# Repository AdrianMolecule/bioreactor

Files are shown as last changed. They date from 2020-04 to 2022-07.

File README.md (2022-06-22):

# bioreactor
Hi there! Welcome to the Bioreactor repository. While a lot of information is still stored in other repositories like Slack, Google Docs and different clouds this is pretty comprehensive and usable.

Please be aware this is work in progress and sometimes the most recent version is under the cloud storage for the specific application.

For software please look under src firmware for most of the code. You will need to use Eclipse and we have a config guide under docs.
The Blocky interpreter will be added soon and initially will be using Visual Studio but that might change.

For electronics you can find descriptive pdf files for all the boards and the corresponding schematics and PCB layouts under electronics. They don't change a lot, so most likely what you see in here is the latest stable board.

For mechanics you can find the Fusion 360 files for the main body under mechanics. Some of the smaller parts that are 3d printed are designed using Tinkercad. Newer ones are done in Fusion 360 or OpenCad as we move away from Tinkercad.

Most of the images and some videos are under docs images. Sometimes an image is worth 1000 words.

There is a boilerplate paper which highlights the generic editing yet it is is just a place to gather paper materials.

We also have a spreadsheet with the parts yet that is a little bit of a moving target as we enhance the design and experiment with newer parts.

Several folders like management-interface, server and controller contain experimental material

Below you can find a brief info about setting up the device, for other questions feel to shoot [us](https://github.com/liquidatom) a message.

## Quick Start

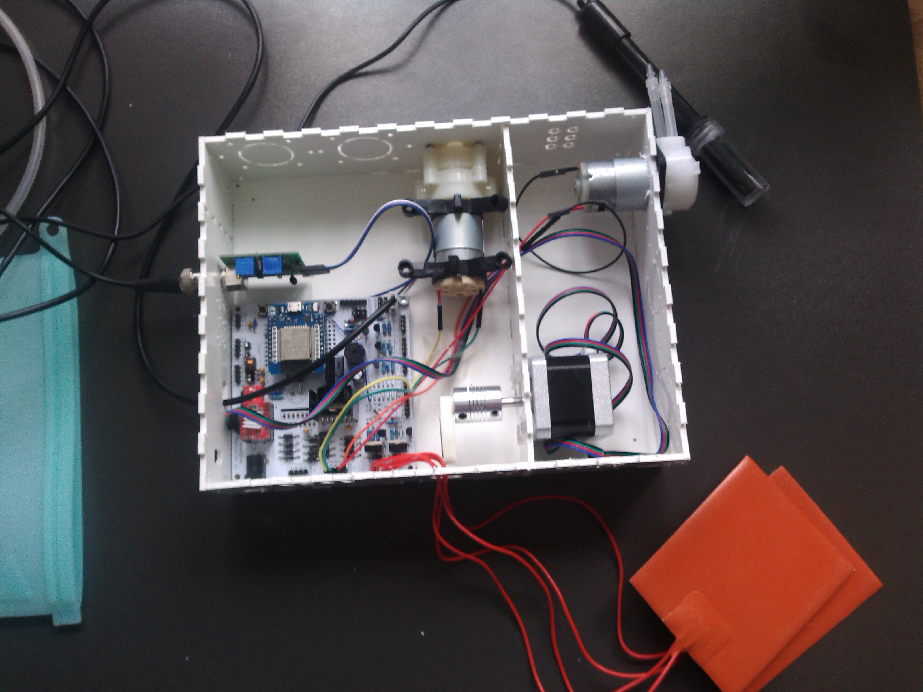
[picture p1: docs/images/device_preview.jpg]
device preview
1. Assemble the device 
2. [Configure eclipse](https://github.com/AdrianMolecule/bioreactor/blob/master/docs/Configuring%20Eclipse%20to%20run%20ESP32.md)  
3. Build and upload firmware
4. Configure bioreactor using [this](https://github.com/AdrianMolecule/bioreactor/tree/master/docs/manual%20bioreactor%20v1.pdf) manual
5. use the ODmeter readme to install the ODMeter

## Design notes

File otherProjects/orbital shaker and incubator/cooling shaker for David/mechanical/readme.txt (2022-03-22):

The f3d files are Fusion360 files for both the CNC machine and 3dPrintig. On request, I can generate stl files for 3d printing and raw files for the specific CNC you have.

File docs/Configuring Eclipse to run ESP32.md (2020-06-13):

This document is about configuring Eclipse to build and run ESP32 firmware. Can be used to configure almost any arduino-like hardware, same way as you can do it in Arduino IDE.

### Prerequirements
I'm using Eclipse 4.15.0, but any with 'Eclipse Marketplace' should work.  
Also i assume your IDE already has C/C++ support, if not, you can easily upgrade it by installing **'Eclipse C/C++ IDE CDT'** plugin from market place

### Steps to run ESP application
1. Open marketplace by clicking Help->Eclipse Marketplace

2. Find and install plugin 'The Arduino Eclipse plugin named Sloeber V4'.  
arduino plugin

3. After installation new menu option 'Arduino' will be added on the top pane. To work with ESP32 you need to open 'Arduino->Preferences->Arduino->Third party index url' and add external url  
<https://adafruit.github.io/arduino-board-index/package_adafruit_index.json>  
<https://raw.githubusercontent.com/espressif/arduino-esp32/gh-pages/package_esp32_index.json>  

4. Then you can enable platform under 'Arduino->Preferences->Arduino->Platforms and Boards' and libraries 'Arduino->Preferences->Arduino->Library Manager'.  
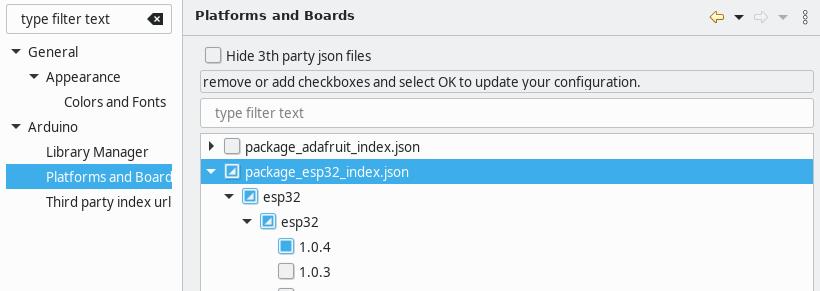
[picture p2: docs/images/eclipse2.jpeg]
sdk lsit
  
There is a useful option 'Arduino->Reattach libraries' which should search through the source code and enable all libraries in Library Manager, though sometimes it misses few of them.

5. After that you just need to import existing project from src/firmware  
If you create a project from scratch, choose File->New->Arduino sketch. In project`s Preferences you want set ESP settings as  depicted below  
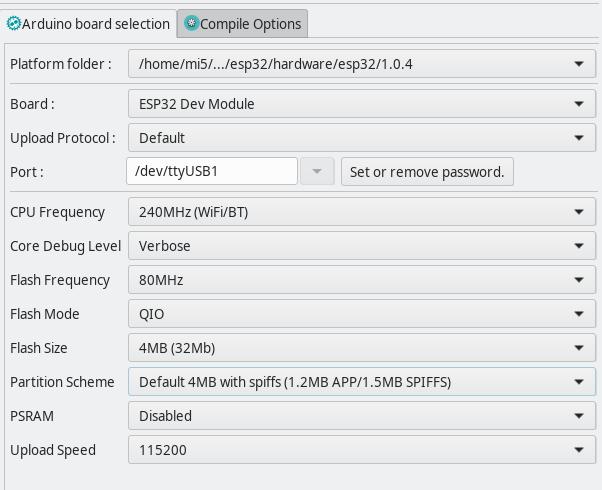
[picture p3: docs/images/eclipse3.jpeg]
new target
  

6. Make sure that eclipse didn't override project files after import (.settings folder and .cproject .project files), otherwise you'll experience weird compilation errors and platform warnings.

**Note**

You may see following errors during compilation
```
platform.h:39:10: error: #include expects "FILENAME" or FILENAME
#include MBEDTLS_CONFIG_FILE
```
to fix this you need to escape quotes for few predefines.  
You need to change definitions in YOUR_ECLIPSE_LOCATION/eclipse/arduinoPlugin/packages/esp32/hardware/esp32/1.0.4/platform.txt  
Substitute  
```
-DMBEDTLS_CONFIG_FILE="mbedtls/esp_config.h"
-DARDUINO_VARIANT="{build.variant}" 
```
with  
```
-DMBEDTLS_CONFIG_FILE='"mbedtls/esp_config.h"'  
-DARDUINO_VARIANT='"{build.variant}"'
```

Now you are all set!

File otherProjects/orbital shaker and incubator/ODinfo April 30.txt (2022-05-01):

OD:-0.00   Sampl:13833  Buffer:13676  sample/buffer:1.01 after:17m 12s at 10 PM April 30th

OD:0.58   Sampl:3556  Buffer (old):13676  sample/buffer:0.26 after:28m 11s at 9:40 AM May 1 so AFTER 12 hours

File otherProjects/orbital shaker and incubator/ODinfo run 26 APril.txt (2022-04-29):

Started at 2 PM on April 26.
Temp: 38 Celsius,  Humidity: 22%.maximum temperature: 39 after: 3h 4m 55s

OD:0.06   Sampl:10661  Buffer:12256  sample/buffer:0.87 8 hours 14 minutes

OD:0.63   Sampl:2852  Buffer (old):12256  sample/buffer:0.23 WARMING UP for another:22h 39m 21s

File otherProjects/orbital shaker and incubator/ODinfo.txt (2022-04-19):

after one dayUsing the untested but presumably accurate ODmeter I did 2 runs
first
Sample/Buffer: 0.23
OD: 0.64   Sampl: 3298   Buffer: 14244
Sample/Buffer: 0.23
OD: 0.64   Sampl: 3299   Buffer: 14244
Sample/Buffer: 0.23
OD: 0.64   Sampl: 3299   Buffer: 14244
Sample/Buffer: 0.23
OD: 0.64   Sampl: 3299   Buffer: 14244
Sample/Buffer: 0.23
OD: 0.64   Sampl: 3299   Buffer: 14244
-----------------
second as a repeat of first after 5 minutes
Sample/Buffer: 0.23
OD: 0.64   Sampl: 3192   Buffer: 13848
Sample/Buffer: 0.23
OD: 0.64   Sampl: 3194   Buffer: 13848
Sample/Buffer: 0.23
OD: 0.64   Sampl: 3196   Buffer: 13848
Sample/Buffer: 0.23

Conclusion: it seems that the OD value is stabile and it might even be correct when osering the high opacity of the aliquot by eye
A short 2 min graph of the absolute lux value in the .png file shows a slow downwards trend but I recall form another earlier test that it woulc reerse the tendency after a while.

after one day repeat ater shaking the cuvete to homogenise. Result
Sample/Buffer: 0.24
OD: 0.63   Sampl: 3395   Buffer: 14321
Sample/Buffer: 0.24
OD: 0.63   Sampl: 3394   Buffer: 14321
Sample/Buffer: 0.24
OD: 0.63   Sampl: 3396   Buffer: 14321
Sample/Buffer: 0.24
OD: 0.62   Sampl: 3401   Buffer: 14321
Sample/Buffer: 0.24

so not too bad and probably makes sense for a lag phase culture to loose some density and probably fluorescence in case that has a noticeable impact on the opacity/scattering. I think the precision is about 5 to 10% for OD.

Second Batch- sorry I have no idea how many hours - probably >10. Another possible problem is that I did not keep the original media so I had to use the preious run media for calibratio. But both the media were prepared the same way so the difference cannot be so high.

OD: 0.74   Sampl: 2621   Buffer: 14321
Sample/Buffer: 0.18
OD: 0.74   Sampl: 2620   Buffer: 14321
Sample/Buffer: 0.18
OD: 0.74   Sampl: 2621   Buffer: 14321
Sample/Buffer: 0.18
OD: 0.74   Sampl: 2620   Buffer: 14321
Sample/Buffer: 0.18
OD: 0.74   Sampl: 2621   Buffer: 14321
==========
Third batch 
Start at 1:40 PM 14 april
buffer value 12419 (OD=.02 compared to previous buffer or .97 bufer batch2/buffer batch3 so the buffer values is not so diferent between batches
Sample/Buffer: 0.99
OD: 0.00   Sampl: 13883   Buffer: 14011
Sample/Buffer: 0.99

After 1 hour 2:40
Sample/Buffer: 1.01
OD: -0.00   Sampl: 13558   Buffer: 13475

After 2 hours 3:50
Sample/Buffer: 0.93
OD: 0.03   Sampl: 13141   Buffer: 14061

After 3 hours 4:40
OD: 0.07   Sampl: 12073   Buffer: 14061
Sample/Buffer: 0.86

After 4 hours 5:40
Sample/Buffer: 1.01
OD: -0.00   Sampl: 13072   Buffer: 12943 or OD=0.06 for initial buffer or 14011
Sample/Buffer: 1.01

After 5ish hours 6:40
OD: 0.00   Sampl: 12952   Buffer: 13050
Sample/Buffer: 0.99

After 6ish hours 7:50
OD:0.01   Sampl:12959  Buffer:13369  sample/buffer:0.97
OD:0.01   Sampl:13088  Buffer:13369  sample/buffer:0.98

at 10:40 after 9 hours it's finally visible
I shook the blank buffer and reinserted itk
OD:0.11   Sampl:12958  Buffer:16512  sample/buffer:0.78
OD:0.11   Sampl:12943  Buffer:16512  sample/buffer:0.78

at 12:40 midnight after 11 hours it's opaque
OD:0.19   Sampl:8689  Buffer (old):13423  sample/buffer:0.65 after:0m 2s

at 9:17 am second day aout 20 hours
OD:0.89   Sampl:1716  Buffer (old):13423  sample/buffer:0.13 after:4m 22s

After 23? hours at 12:40 PM
OD:0.51   Sampl:3792  Buffer:12256  sample/buffer:0.31 after:1h 2m 32s

============================================
4th batch started at 11:30 am Thursday April 15
OD:0.12   Sampl:9278  Buffer:12256  sample/buffer:0.76 after:0m 29s

at 3:40 
OD:-0.02   Sampl:12937  Buffer:12256  sample/buffer:1.06 after:4h 6m 1s

OD:0.04   Sampl:11178  Buffer:12256  sample/buffer:0.91 after:7h 44m 38s
OD:-0.08   Sampl:14644  Buffer:12256  sample/buffer:1.19 after:7h 49m 15s LAG

OD:0.87   Sampl:1666  Buffer:12256  sample/buffer:0.14 after:16h 56m 12s EXPO OR STATIONARY OR DEATHE

============================
5th started at 4 AM
using old blank buffer value, expect expo to be between 9 and 20 hours based on previous batches

at 10 AM
OD:-0.01   Sampl:12614  Buffer (old):12256  sample/buffer:1.03 after:0m 44s I need to ADD 6 hours to all this. So after 6 hours no significant  growth LAG

at 11:17 AM
OD:-0.03   Sampl:13060  Buffer (old):12256  sample/buffer:1.07 after:1h 17m 33s LAG REAL TIME 7.17

at 2:33 PM
OD:0.34   Sampl:5563  Buffer (old):12256  sample/buffer:0.45 after:4h 33m 46s EXPONENTIAL REAL TIME 10h 33 min

at 6 PM
OD:0.53   Sampl:3583  Buffer (old):12256  sample/buffer:0.29 after:7h 59m 37s REAL TIME 14 hours

at 7:40
OD:0.59   Sampl:3243  Buffer (old):12256  sample/buffer:0.26 after:9h 38m 46s  REAL TIME 15.4 hours

at 9:35
OD:0.63   Sampl:2902  Buffer (old):12256  sample/buffer:0.24 after:11h 36m 8s RT 17.36 hours

at 10:42
OD:0.60   Sampl:3109  Buffer (old):12256  sample/buffer:0.25 after:13h 43m 18s 18.43 RT 18.43 hours

at 1:20
OD:0.65   Sampl:2743  Buffer (old):12256  sample/buffer:0.22 after:16m 41s RT 21:30

at 9:15
OD:0.64   Sampl:2786  Buffer (old):12256  sample/buffer:0.23 after:16m 23s RT 29:30

There is a large overwhelmig hange from when I start measurement. I can be because of temperature of the sensor, LED, cuvette or culture
The is a large change between shaking and measure versus sedimented measure. There is very little change depending on how much the cuvette is inserted.
Q1. When does it stabilize it ever?
Q2 is it because of the cuette and content or just because of the heating of LED/sensor
Here are the numbers:
OD:0.29   Sampl:6237  Buffer (old):12256  sample/buffer:0.51 after:0m 0s

OD:0.55   Sampl:3424  Buffer (old):12256  sample/buffer:0.28 after:7m 14s
OD:0.54   Sampl:3496  Buffer (old):12256  sample/buffer:0.29 after:8m 25s

OD:0.49   Sampl:3953  Buffer (old):12256  sample/buffer:0.32 after:16m 17s

OD:0.47   Sampl:4106  Buffer (old):12256  sample/buffer:0.34 after:17m 17s

SHAKING
clearly if I shake the cuvette after 30 minutes of settle we go from .45 ->.70 in this case. So cells or dead cells go to the ottom and it makes a huge diference.
after a while OD=.18 unshaken  and then OD:0.69   after shaking
put old  sample skaken ->.68 went back to 32 after a 40 min pause  and back to .68 when shaken. Repeated that ater 24 hours- when  clear OD=o and when well shaken OD=.69

WARM_UP

so its proabl the led or resistor that starts od=0 and stabilizes to .32 after 15 min fine after

TEST with no cuvette
OD:-0.32   Sampl:25770  Buffer (old):12256  sample/buffer:2.10 after:0m 0s
OD:-0.12   Sampl:16067  Buffer (old):12256  sample/buffer:1.31 after:1m 16s
OD:-0.05   Sampl:13689  Buffer (old):12256  sample/buffer:1.12 after:2m 4s
OD:0.15   Sampl:8739  Buffer (old):12256  sample/buffer:0.71 after:20m 59s
OD:0.11   Sampl:9483  Buffer (old):12256  sample/buffer:0.77 after:2h 13m 11s

OD:0.09   Sampl:9974  Buffer (old):12256  sample/buffer:0.81 after:5m 15s
OD:0.14   Sampl:8863  Buffer (old):12256  sample/buffer:0.72 after:15m 0s
OD:0.13   Sampl:9181  Buffer (old):12256  sample/buffer:0.75 after:1h 45m 59s

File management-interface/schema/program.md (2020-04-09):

# Schema for bioreactor protocols

This page describes a JSON schema for representing bioreactor protocols. A protocol is a sequence of steps that the bioreactor should go through. For example, a step might involve heating bringing the bioreactor to a certain temperature or to a certain pH level, or it might involve simply waiting for a certain amount of time.

If you are not familiar with JSON (javascript object notation), read this [primer](https://www.json.org/json-en.html) first.

This schema is written in terms of [Golang structs](https://blog.golang.org/json) but can be used from any language.

### Example protocol

Here is an example of a program that:
 - brings the temperature to 220°C and holds it there for 3 hours, then
 - brings pH to 3, then
 - turns on a cyan light for 10 minutes

```json
{
    "name": "test protocol",
    "root": {
        "steps": [
            {
                "hold_temperature_at": {
                    "temperature": 220,
                    "duration": 10800,
                },
                "bring_ph_to": {
                    "ph": 3,
                },
                "hold_lighting_at": {
                    "color": {
                        "red": 0,
                        "green": 255,
                        "blue": 255,
                    }
                    "duration": 600,
                }
            }
        ]
    }
}
```

### BringTemperatureTo

BringTemperatureTo is a step that causes the bioreactor to bring the temperature to a certain level and then move on to the next step.

```go
type BringTemperatureTo struct {
    TemperatureCelsuis float64  // the desired temperature in degrees Celsius
    MaxRate float64             // the maximum rate of heating, in degrees Celsius per second
}
```

Example
```json
{
    "temperature_celsius": 220,   // 220°C
    "max_rate": 3,                // heat at 3 degrees per second
}
```

### HoldTemperatureAt

HoldTemperatureAt is a step that causes the bioreactor to bring the temperature to a certain level and then hold it there for a certain amount of time.

```go
type HoldTemperatureAt struct {
    TemperatureCelsuis float64  // the desired temperature in degrees Celsius
    MaxRate *float64            // the maximum rate of heating, in degrees Celsius per second
    Duration time.Duration      // the amount of time to hold the temperature at this level
}
```

Example
```json
{
    "temperature_celsius": 220,   // 220°C
    "max_rate": 3,                // heat at 3 degrees per second
    "duration": 10800,            // 10800 seconds = 3 hours
}
```

### BringPhTo

BringPhTo is a step that causes the bioreactor to bring the pH to a certain level and then move on to the next step.

```go
type BringPhTo struct {
    PH float64      // the desired pH
    MaxRate float64 // the maximum rate of heating, in degrees Celsius per second
}
```

Example
```json
{
    "ph": 5,                      // 220°C
    "max_rate": 3,                // heat at 3 degrees per second
    "duration": 10800,            // 10800 seconds = 3 hours
}
```

### HoldPhAt

HoldPhAt is a step that causes the bioreactor to bring the pH to a certain level and then hold it there for a certain amount of time.

```go
type HoldTemperatureAt struct {
    PH float64               // the desired temperature in degrees Celsius
    MaxRate float64          // the maximum rate of heating, in degrees Celsius per second
    Duration time.Duration   // the amount of time to hold the temperature at this level
}
```

Example
```json
{
    "ph": 5,
    "max_rate": 3,         // heat at 3 degrees per second
    "duration": 10800,     // 10800 seconds = 3 hours
}
```

### HoldLightingAt

HoldLightingAt holds the lighting at a set color and brightness for a certain amount of time.

```go
type Color struct {
    Red int    // the red component of color (0..255)
    Green int  // the green component of color (0..255)
    Blue int   // the blue component of color (0..255)
}

type HoldLightingAt struct {
    Color *Color   // The red, green, and blue components of the color
    Lumens int     // Brightness in lumens
    Duration time.Duration  // duration to hold the lighting at this point
}
```

Example:
```json
{
    "color": {
        "red": 0,
        "green": 255,
        "blue": 255,
    },
    "lumens": 600,
    "duration": 600,   // 600 seconds = 10 minutes
}
```

### Wait

Wait instructs the bioreactor to wait passively for a set amount of time

```go
type Wait struct {
    Duration time.Duration
}
```

Example:
```json
{
    "duration": 10800,   // 3 hours
}
```

### Sequence

A sequence instructs the bioreactor to execute a series of steps, one after another

```go
type Sequence struct {
    Steps []*Step
}
```

Example:
```json
{
    "steps": [
        "hold_temperature_at": {
            "temperature": 220,
            "duration": 10800,
        },
        "bring_ph_to": {
            "ph": 3,
        },
        "hold_lighting_at": {
            "color": {
                "red": 0,
                "green": 255,
                "blue": 255,
            }
            "duration": 600,
        }
    ]
}
```

### Step

A step is a union type that can be one of several types. Exactly one of the pointer members is non-nil.

```go
type Step struct {
    BringTemperatureTo *BringTemperatureTo
    HoldTemperatureAt *HoldTemperatureAt
    BringPhTo *BringPhTo
    HoldPhAt *HoldPhAt
    HoldLightingAt *HoldLightingAt
    Wait *Wait
    Sequence *Sequence
}
```

### Program

A program has a name and a root step. Exactly one of the pointer members are non-nil.

```go
type Program struct {
    Name string
    Root *Step
}
```

Example:
```json
{
    "name": "test protocol",
    "root": {
        "steps": [
            {
                "hold_temperature_at": {
                    "temperature": 220,
                    "duration": 10800,
                },
                "bring_ph_to": {
                    "ph": 3,
                },
                "hold_lighting_at": {
                    "color": {
                        "red": 0,
                        "green": 255,
                        "blue": 255,
                    }
                    "duration": 600,
                }
            }
        ]
    }
}
```

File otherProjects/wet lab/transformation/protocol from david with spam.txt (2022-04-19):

you calculate upon the known transformation efficiency from a plasmid and the colony forming units of that plasmid in different selection markers, in this case all the plasmids I transformed are the pDawn with different content (taq, pfu, rt) all in LB-Kan
6:37
plus controls
6:37
all treated with the same procedure:
6:40
grow your cells (BL21 DE3) to approx. 0.5 OD or just a 1/20 of the initial overnight inoculum, leave it for 3-4 hrs, (10ml culture vol)
6:44
after that you spin down and wash with simple cold deionized, autoclaved water
6:44
twice
6:45
water from the fridge (4-8°C)
6:47
then  make aliquots of 1ml and then split it 100uL in independent tubes
6:47
you can keep them in the fridge over night or
6:47
add appro 10ng of plasmids per tube, then move them to the freezer for no more than 5 min
6:48
adjust your microwave to 300w and give them a pulse for 30sec
6:48
add 1m fresh, new sterile LB
6:49
incubate at 37°C for 45 min to 1hr
6:49
plate on agarLB+ antibiotics
6:51
incubate a 37°C or desired temp (pDawn grows better around 25°C)
6:53
and voilá!

Adrian Molecule  6:56 PM
that sounds pretty simple and straightforward. So you mean you count the colonies from the transformed bacteria that fluoresce versus bacteria that does not fluoresce on the same plate?

David J.Castillo  6:56 PM
in this case they are not fluorescent but I can try like that, in this case are those that acquire the resistance with the transformed plasmid

Adrian Molecule  6:57 PM
or 2 plates - one negative untransformed plate  versus a trnasformed one?

David J.Castillo  6:57 PM
the plain BL21 DE3 dies in the presence of Kan
6:57
yeah
6:57
exactly

Adrian Molecule  6:59 PM
so 2 plates: one with Kan and transformed bacteria. One with no Kan and BL21 DE3. The transformed plate will have much less colonies (edited) 

David J.Castillo  7:02 PM
Plate 1: LB-Kan plus BL21-DE3 and the kan resistant plasmid = Colonies; Plate 2 LB-Kan plus BL21-DE3, with NO plasmid, they die; Plate 3 LB- plus BL21-DE3 with no plasmid= lots of colonies
7:03
I will patch the colonies on a new fresh LB-Kan and run some mini preps to confirm.

Adrian Molecule  7:14 PM
so the difference between Plate 1 and 3 will tell you how many of the plasmids made it in the bacteria. Normally is 1 in 10 000 -20000

David J.Castillo  7:14 PM
yup

Adrian Molecule  7:15 PM
and you tied this protocol with 3 types of plasmids and obtained a high transformation rate
7:16
it's fast and does not require CaCL2 reagents

David J.Castillo  7:16 PM
yup
7:17
faster, cheaper

Adrian Molecule  7:17 PM
the trick is to note the numbers because the microwave seconds depend on the quantity of liquid

David J.Castillo  7:19 PM
100uL per tube
7:20
more or less

Adrian Molecule  7:20 PM
I would probably do something like this. Take a 100 ml flask with 50 ml water and microwave for 30 seconds.
7:20
measure the temperatre

David J.Castillo  7:20 PM
in my case the microwave i got the manual tells how you can calculate the power

Adrian Molecule  7:21 PM
then adjust the time for any other microwave to heat the same quantity of liquid at the same temperature
7:21
it's not the power but the heat that the best way to calculate

David J.Castillo  7:21 PM
the critical part is maintaining the same power
7:22
ok
7:22
yeah the resulting heat
7:22
I read a note on epicurious about that hold on

Adrian Molecule  7:22 PM
with the same power you'll get dierent results for microwaes of dierent olumes

David J.Castillo  7:23 PM
https://www.epicurious.com/expert-advice/how-to-find-adjust-wattage-power-of-microwave-oven-article
EpicuriousEpicurious
The Simple Trick to Cooking Food Perfectly in the Microwave
Just how well do you know your microwave?
Apr 12th, 2016 (173 kB)
https://www.epicurious.com/expert-advice/how-to-find-adjust-wattage-power-of-microwave-oven-article

Adrian Molecule  7:23 PM
you can tell my keyboard is missing f and b ...

https://youtu.be/t9k8HFL88kk quantify bands using imagej

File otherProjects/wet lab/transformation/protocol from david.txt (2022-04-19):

Full protocol https://asm.org/ASM/media/Protocol-Images/Transformation-of-Escherichia-coli-Made-Competent-by-Calcium-Chloride-Protocol.pdf?ext=.pdf
you calculate upon the known transformation efficiency from a plasmid and the colony forming units of that plasmid in different selection markers, in this case all the plasmids I transformed are the pDawn with different content (taq, pfu, rt) all in LB-Kan
6:37
plus controls
6:37
all treated with the same procedure:

grow your cells (BL21 DE3) to approx. 0.5 OD or just a 1/20 of the initial overnight inoculum, leave it for 3-4 hrs, (10ml culture vol)
after that you spin down and wash with simple cold deionized, autoclaved water
twice

water from the fridge (4-8°C)

then  make aliquots of 1ml and then split it 100uL in independent tubes

you can keep them in the fridge over night or

add appro 10ng of plasmids per tube, then move them to the freezer for no more than 5 min

adjust your microwave to 300w and give them a pulse for 30sec

add 1m fresh, new sterile LB

incubate at 37°C for 45 min to 1hr

plate on agarLB+ antibiotics

incubate a 37°C or desired temp (pDawn grows better around 25°C)

and voilá!

Adrian Molecule  6:56 PM
that sounds pretty simple and straightforward. So you mean you count the colonies from the transformed bacteria that fluoresce versus bacteria that does not fluoresce on the same plate?

David J.Castillo  6:56 PM
in this case they are not fluorescent but I can try like that, in this case are those that acquire the resistance with the transformed plasmid

Adrian Molecule  6:57 PM
or 2 plates - one negative untransformed plate  versus a trnasformed one?

David J.Castillo  6:57 PM
the plain BL21 DE3 dies in the presence of Kan
6:57
yeah
6:57
exactly

Adrian Molecule  6:59 PM
so 2 plates: one with Kan and transformed bacteria. One with no Kan and BL21 DE3. The transformed plate will have much less colonies (edited) 

David J.Castillo  7:02 PM
Plate 1: LB-Kan plus BL21-DE3 and the kan resistant plasmid = Colonies; Plate 2 LB-Kan plus BL21-DE3, with NO plasmid, they die; Plate 3 LB- plus BL21-DE3 with no plasmid= lots of colonies
7:03
I will patch the colonies on a new fresh LB-Kan and run some mini preps to confirm.

Adrian Molecule  7:14 PM
so the difference between Plate 1 and 3 will tell you how many of the plasmids made it in the bacteria. Normally is 1 in 10 000 -20000

David J.Castillo  7:14 PM
yup

Adrian Molecule  7:15 PM
and you tied this protocol with 3 types of plasmids and obtained a high transformation rate
7:16
it's fast and does not require CaCL2 reagents

David J.Castillo  7:16 PM
yup
7:17
faster, cheaper

Adrian Molecule  7:17 PM
the trick is to note the numbers because the microwave seconds depend on the quantity of liquid

David J.Castillo  7:19 PM
100uL per tube
7:20
more or less

Adrian Molecule  7:20 PM
I would probably do something like this. Take a 100 ml flask with 50 ml water and microwave for 30 seconds.
7:20
measure the temperatre

David J.Castillo  7:20 PM
in my case the microwave i got the manual tells how you can calculate the power

Adrian Molecule  7:21 PM
then adjust the time for any other microwave to heat the same quantity of liquid at the same temperature
7:21
it's not the power but the heat that the best way to calculate

David J.Castillo  7:21 PM
the critical part is maintaining the same power
7:22
ok
7:22
yeah the resulting heat
7:22
I read a note on epicurious about that hold on

Adrian Molecule  7:22 PM
with the same power you'll get dierent results for microwaes of dierent olumes

David J.Castillo  7:23 PM
https://www.epicurious.com/expert-advice/how-to-find-adjust-wattage-power-of-microwave-oven-article
EpicuriousEpicurious
The Simple Trick to Cooking Food Perfectly in the Microwave
Just how well do you know your microwave?
Apr 12th, 2016 (173 kB)
https://www.epicurious.com/expert-advice/how-to-find-adjust-wattage-power-of-microwave-oven-article

Adrian Molecule  7:23 PM
you can tell my keyboard is missing f and b ...

David J.Castillo  7:24 PM
hehehe

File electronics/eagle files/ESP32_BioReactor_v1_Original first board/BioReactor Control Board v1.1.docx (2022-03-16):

“Fighting viruses require expensive reagents. For cheap and quality reagents you need a bioreactor, a controlled environment growth chamber.”

# Introduction*

## 1. Problem and Background

“Detecting the virus or creating solutions like vaccines require reagents.

To run detection you need reagents for each test. Reagents are expensive and many are unavailable due to current demand. There is an imperious need to create an abundant yet qualitative alternative inexpensive source for these reagents. There are several labs working on this, notably the FreeGenes to mention one of the leaders.

The only way to produce reagents of quality in usable quantities is to use a bioreactor. Commercial bioreactors cost thousands or tens of thousands. That does not reflect manufacturing costs. Existing open source designs are not usable, abandoned prototypes, work in progress or they accommodate only some types of cells.

That's why this is important. A cheap alternative to commercial bioreactors that would cost less than € 200 would solve this and also make possible the rest of the other initiatives.

A bioreactor is a chamber where cells are grown under very specific conditions. For instance controlling temperature, Oxygen, pH, Optical Density, Lighting, Weight etc.

We will create a wave bioreactor. Based on our non-exhaustive comparison of industrial and non-industrial bioreactors only wave bioreactors can reliably produce high quality results for advanced types of cells.“

Source: https://docs.google.com/document/d/1ho2kqETR3HEMr810e-MaQIFVknhwcr6aLd0Yrn7DFjk/edit#

# Control board version 1.0 Description

The initial version of the board is designed as a prototype consolidation of the functions necessary to run a small, low-cost reagent manufacturing machine – a bioreactor. The following is the circuit schematic and an image of the 100mm x 100mm double-sided PCB.

The board contains an ESP32 D1 Mini Module to control on-board driver and interface circuits for the machine.

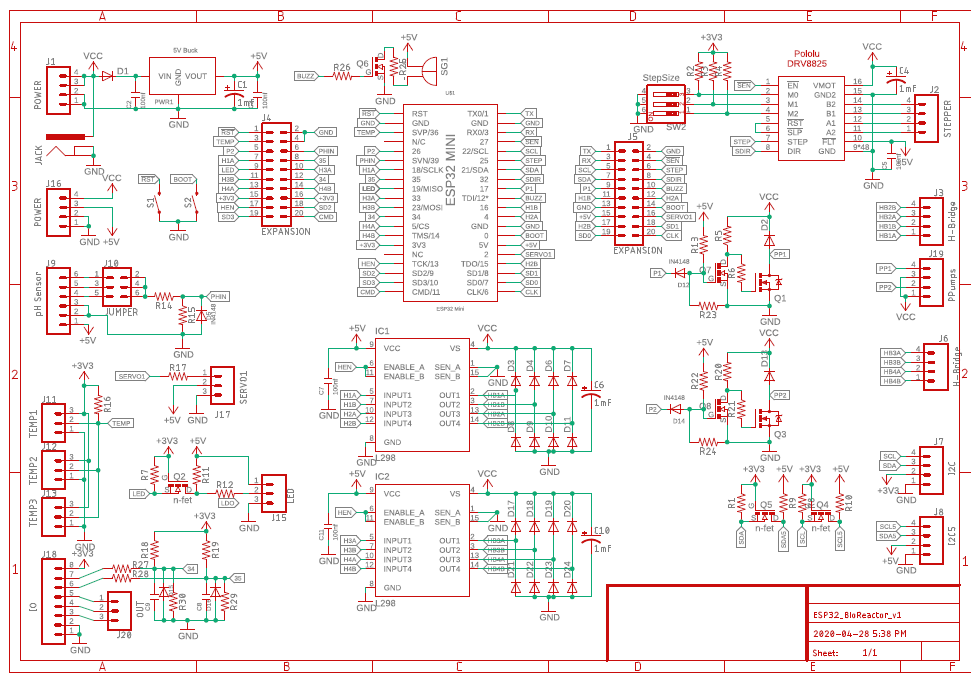
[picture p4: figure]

ESP32_BioReactor_v1 Schematic

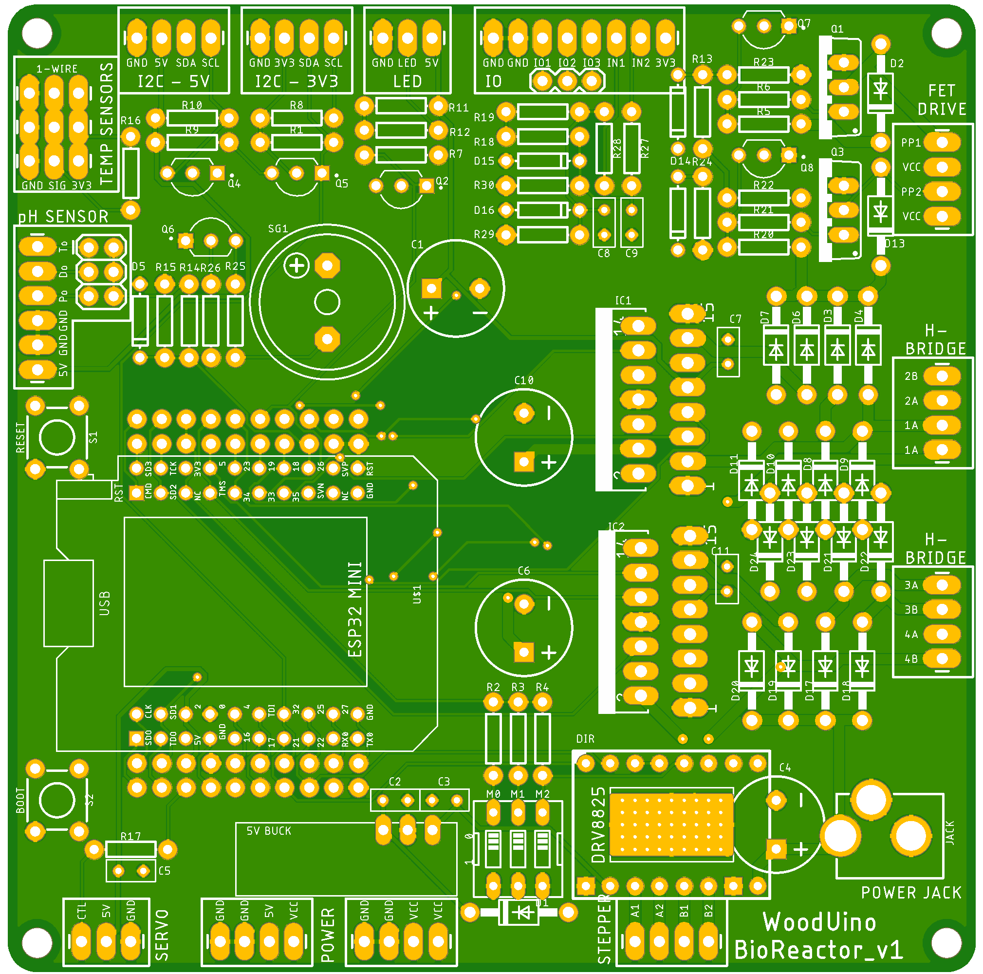
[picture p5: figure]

ESP32_BioReactor_v1 Circuit Board Layout

This version of the PCB includes support for the following features:

## 2. Rocking Mechanism

The rocking mechanism consists of a tray that can be moved in one plane from side to side to keep the chemicals agitated. Two designs are included to allow the control of this rocking motion to be performed by either a stepper motor or a servo.

STEPPER MOTOR: The DRV8825 stepper motor driver is the popular low-cost dual inline module used to control NEMA 17 motors often found in small drawing machines and 3D printers. The ESP32 controls the motor’s STEP [25] and DIRECTION [32], and includes an ENABLE [27] to activate (0) / deactivate (1) the motor power.

The stepper driver module is powered directly from the main supply voltage (typically 12V) delivered to the board. A 4-pin connector [STEPPER: A1, A2, B1, B2] allows direct connection to a typical NEMA 17 dual-phase stepper motor. In addition, three DIP switches on the board set the micro-stepping feature from FULL-STEP to 1/16th STEP for fine control of the motor speed and power as follows.

STEP SIZE | M0 | M1 | M2
FULL | 0 | 0 | 0
HALF STEP | 1 | 0 | 0
QUARTER STEP | 0 | 1 | 0
EIGHTH STEP | 1 | 1 | 0
SIXTEENTH STEP | 1 | 1 | 1

The module contains a small trimpot that allows the user to set the supply current necessary to operate the particular stepper motor being used. To minimize power dissipation, this trimpot should be adjusted to operate the stepper motor just above its stall current.

In addition, it is important to note that the A4988 Stepper Driver Module is a pin-for-pin compatible device and can be substituted with no code or hardware changes.

SERVO MOTOR: A servo motor connection [2] is provided to control a MG995 or similar power servo from the 5V supply. If a larger servo motor is to be used, it is recommended that it is connected to its own supply voltage.

## 3. Peristaltic Pumps, Air Pumps and Heater Drivers

The board consists of two high-power dual H-bridges and two power-FETs to control the array of peristaltic pumps, air pumps and heater/cooler systems that may be present. While the design requirements of the machine may change, these power drivers are not dedicated to operate specific external devices, allowing the user to mix-and-match them as needed. The functionality provided is as follows:

H-BRIDGES: Two dual H-Bridge drivers – using the L298N - are included to provide 4 independent bi-directional pulse-width modulated (PWM) 12V outputs. The L298N has been around for many years and is robust, reliable and easy to heatsink, if necessary. Both devices share a common ENABLE [13] pin to activate (1) / deactivate (0) all four of the outputs.

Each of the H-Bridge drivers uses two inputs to control its two output pins. The pins used are as follows:

H-BRIDGE | INPUT A | INPUT B | CONNECTOR OUTPUT
H1 | H1A [18] | H1B [16] | HB1A, HB1B
H2 | H2A [4] | H2B [15] | HB2A, HB2B
H3 | H3A [33] | H3B [23] | HB3A, HB3B
H4 | H4A [5] | H4B [14] | HB4A, HB4B

In operation, one INPUT can be used as a FORWARD (REVERSE) DIRECTION while the other INPUT pin can be used to control power through PWM. Note that the “value” of the PWM will depend on the polarity of the DIRECTION input.

POWER FETS: Two power n-channel FETs are included to provide unidirectional control to two independent 12V devices, each connected between VCC and the OUTPUT. These connections can ON/OFF control 12V devices directly, and mains-operated devices using an external opto-coupled solid-state relay (SSR) or relay. In addition, the power delivered to each OUTPUT can be controlled using PWM.

The power FETs are controlled by P1 [17] and P2 [26] and output on connections PP1 and PP2. The pre-driver circuitry for each power FET allows the user to change the power-on state of the output through component population choices, as follows:

POWER FET | POWER-ON STATE | POPULATE | DEPOPULATE | CONNECTOR OUTPUT
P1 | OFF (DEFAULT) | R13, D12 (fwd) | R23 | PP1, VCC
P1 | ON | R23, D12 (rev) | R13
P2 | OFF (DEFAULT) | R22, D14 (fwd) | R24 | PP2, VCC
P2 | ON | R24, D14 (rev) | R22

## 4. I2C OLED [LCD] Display & Sensors

The board offers two I2C communication ports, one at 3.3V and the other at 5V, to connect displays, sensors (including the BH1750 optical density sensor), real-time clocks and other I2C connected devices. The I2C uses the ESP32’s default pins for SCL [22] and SDA [21]. The logic levels from the ESP32 are also shifted to run at 5V using discrete FET bidirectional level converters to allow lots of flexibility.

## 5. Addressable LED Array / Panel

The board sports a single serial OUTPUT [19] to connect one or more addressable LEDs, based on the WS2812B NEOPIXEL. The logic levels from the ESP32 are shifted to run from the 5V using a discrete FET bidirectional level converter to allow the driving of standard strips or panels of these LEDs. Suitable libraries (Adafruit, FastLED) offer simple control of the red, green and blue (rgb) LEDs of the WS2812B chips, while also providing more sophisticated support for using hue, saturation and light intensity (HSV) and other colour models.

The on-board 5V supply is capable of supplying up to 1.5A, so a good ‘rule-of-thumb’ would be to limit the number of WS2812B NEOPIXELs to ~64. If more are required – for increased coverage or intensity, for instance – it will be necessary to power them with an external 5V supply.

## 6. Temperature Sensors

Provision on the board is made to support three DS18B20 temperature sensors that run on 3.3V and use the Dallas Semiconductor “1-WIRE” protocol [36]. While there are three separate output connectors, the simple protocol allows this number to be increased to support mode devices, if needed.

## 7. pH Sensor

An INPUT connection is provided [39] to support a pH Sensor and its associated control module. As the pH module is powered from the 5V supply, a resistor voltage divider is provided (R14, R15) – along with a 3.3V Zener for protection – to limit the analogue input range to ~3V. In addition, three jumpers are provided allowing selectable connection to the three pH sensor module analogue outputs.

## 8. Alert Buzzer

A single buzzer is provided [12] to allow for audible feedback. A small-signal FET is used to provide power to the buzzer through a current limiting resistor (R25), which can be selected based on the audible level required.

## 9. Expansion Port

A small expansion port is provided to allow the connection of two INPUTs [34 and 35] which are protected with resistor pull-up (R18, R19 respectively), pull-down (R30, R29, resp.), voltage dividers (R27|| R30 and R28 || R29, respectively) for flexibility. 3.3V Zener diodes are also provided for protection and the optional 0.1uF capacitors (C9, C8) can be used for simple low-pass filtering and button debouncing. 3.3V and GND connections are also provided.

In addition, connections to 3 INPUT/OUTPUTs are also provided. These are undedicated and can be ‘jumpered’ to any unused IO pins. All signals are 3.3V

## 10. Power In/Out

Main power (typically 12V) can be connected to the board through a standard 5.5/2.1mm power jack or through pairs of connector pins. An additional set of power pins is also provided for connections to 12V, 5V and GND for off-board power.

## 11. Miscellaneous

The board also features a reset switch – to restart the ESP32 - and a boot switch that may be needed when new software is being downloaded to the ESP32.

# ESP32 D1 Mini Pin Connections

The following table shows the ESP32 D1 Mini connections used:

ESP32 Pin | Function | | ESP32 Pin | Function
!RST | ESP32 Reset | | 1 / TXD | Transmit Data (USB)
GND | Supply 0v | | 3 / RXD | Receive Data (USB)
36 / TEMP | Temp sensors I/P | | 27 / !SEN | Stepper !ENABLE
26 / P2 | Power FET 2 O/P | | 22 / SCL | I2C SCL
39 / PHIN | pH sensor I/P | | 25 / STEP | Stepper STEP
18 / H1A | H-Bridge 1A | | 21 / SDA | I2C SDA
35 | General purpose I/P | | 32 / SDIR | Stepper DIRECTION
19 / LED | LED O/P | | 17 / P1 | Power FET 1 O/P
33 / H3A | H-Bridge 3A | | 12 / BUZZ | Buzzer O/P
23 / H3B | H-Bridge 3B | | 16 / H1B | H-Bridge 1B
34 | General purpose I/P | | 4 / H2A | H-Bridge 2A
5 / H4A | H-Bridge 4A | | 0 / BOOT | ESP32 Boot / Flash
14 / H4B | H-Bridge 4B | | 5V | 5V Power I/P
3V3 | 3.3V OP | | 2 / SERVO1 | Servo CTL O/P
13 / HEN | H-Bridge Enable O/P | | 15 / H2B | H-Bridge 2B
SD2 | Internal FLASH | | SD1 | Internal FLASH
SD3 | Internal FLASH | | SD0 | Internal FLASH
CMD | Internal FLASH | | CLK | Internal FLASH

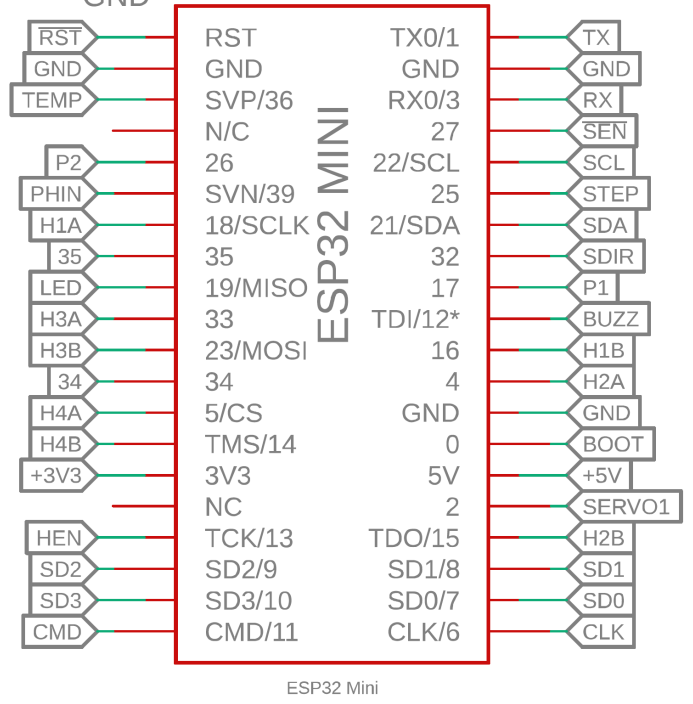
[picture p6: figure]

# Bill Of Materials (BOM)

The following is a Bill of Materials for the board.

Qty | Value | Device | Parts
7 | 100nf | CERAMIC DISC - 0.1" (14) | C2, C3, C5, C7, C8, C9, C11
4 | 1000uF | 1000UF RADIAL 5MM 25V 20% (15) | C1, C4, C6, C10
20 | 10K | 10K 1/4W 1% Axial | All others ***
5 | 4K7 | 4K7 1/4W 1% Axial | R21,R6, R26, R16,R15
1 | 3K3 | 3K3 1/4W 1% Axial | R14
5 | 200Ω | 200 1/4W 1% Axial | R12, R17, R25, R27, R28
19 | 1N4001/Schottky | 1N4001 / 1N5819 (5) | D1, D2, D13, D3-D11, D17-D24
2 | IN4148 / IN914 | Small signal Axial (4) | D12, D14
3 | ZENER | 3V3 Zener Axial (3) | D5, D15, D16
6 | N-FET | 2N7000 T092 (11) | Q2, Q4, Q5, Q6, Q7, Q8
1 | 5V BUCK | 5VBUCK (1) | 5VBUCK
1 | POLOLU-DRV8825 | POLOLU-DRV8825 (6) | DR1
1 | ESP32 D1 MINI | ESP32 D1 MINI (7) | U1
1 | BUZZER | 12085 BUZZER (2) | SG1
2 | N-Power FET | IRF540 / FQP50N06 TO220 (8) | Q1, Q3
1 | JUMPER | CONN_03X2FEMALE 0.1" | J10
2 | L298N | L298 ZIP-15 (9) | IC1, IC2
2 | SWITCH | MOMENTARY SPST 6.0MM (12) | S1, S2
1 | POWER_JACK | POWER_JACKPTH_LOCK (13) | JACK
1 | STEPs Switch | SW_DIP-3 (10) | SW2

Note that several of the resistors listed as 10K (R18, R19, R29, R30) may have their value changed or not be populated (R13, R23, R22, R24) depending on the use of that part of the circuit.

## 12. Buying Notes

The following are some suggestions for purchasing the components used on the board. In many cases, substitutions are acceptable.

1. 5V Buck Converter Power Supply Module: https://www.aliexpress.com/item/32326346960.html
2. Passive buzzer 12A05 2KHz: https://www.aliexpress.com/item/4000133619336.html
3. 3.3V Zener diode (1N4728A 3V3): https://www.aliexpress.com/item/33036174099.html
4. 1N4148 small signal diode: https://www.aliexpress.com/item/33035453991.html
5. IN4001 / 1N5819 Schottky diode: https://www.aliexpress.com/item/32854074561.html
6. DRV8825 Polulu stepper driver: https://www.aliexpress.com/item/1000005739591.html
7. ESP32 D1 Mini board: https://www.aliexpress.com/item/4000650306925.html
8. 50N06 N-Power FET: https://www.aliexpress.com/item/32823515287.html
9. L298N ZIP-15: https://www.aliexpress.com/item/32867965978.html
10. Slide Toggle 3-way DIP switch: https://www.aliexpress.com/item/32892007978.html
11. 2N7000 N-ch MOSFET: https://www.aliexpress.com/item/4000515871375.html
12. 6mm Momentary tactile switch: https://www.aliexpress.com/item/32961272650.html
13. 5.5mm 2.1mm Power Jack: https://www.aliexpress.com/item/32730260523.html
14. 100nF (0.1”) ceramic cap.: https://www.aliexpress.com/item/32868001945.html
15. 1000uF 25V electrolytic cap.: https://www.aliexpress.com/item/32506590473.html

8 Adrian Jones :: WoodUino r1.1.200430

ESP32 BioReactor Control Board

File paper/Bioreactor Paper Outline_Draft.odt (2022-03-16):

Design, assembly and distribution of a low cost, automated, open source Bioreactor using a light inducible protein synthesis system for the production of molecular biology reagents required in COVID19 and other viral diseases diagnostics.

Adrian Philip, Alexander Ikolavie, David J. Castillo-Cornejo, Alexander Klenov, Therese Schachner,

Keywords:

Collaborative biotechnology, open electronics, open genes distribution, DIYBiotechnology, Protein engineering, Additive manufacturing, COVI19 testing, citizen science, technology democratization, optogenetics, Makers, Biohacking, portable devices. viral load. fluorescent proteins.

Authors affiliations and institutions:

Ottawa Bioscience, Ontario Canada,

Glyxon Biolabs, Mexico City, Mexico

Abstract

The objective of the present work was to develop a low cost, portable, modular, easy distribution, and minimal maintenance automated bioreactor, accompanied with a comprehensive protein biosynthesis system that relies on an optogenetic induction switch. This open source, modular, reusable wave bioreactor with a controllable environment allows for the production of reagents, including those required for the COVID-19 test to detect the coronavirus. Since this bioreactor costs less than $300, it provides an affordable solution to the issue of reagents that are often expensive or difficult to obtain, resulting in the increased accessibility of bioreactors and reagents for research and production purposes. Within this bioreactor, variables such as temperature, optical density, pH, and dissolved oxygen can be controlled in order to create the environments necessary to produce cells like bacteria, yeast, insect or mammalian cells suitable for production of reagent proteins, antibodies, viral vectors, etc. A team of members from various geographic regions collaborated remotely to design the bioreactor through online communication channels, as well as implement and test the bioreactor in the labs to which team members had access. We are sharing the open source documentation and a production organism kit with the materials to build the bioreactor so that it can be built at an affordable cost.

Introduction

During the winter of 2019, a novel zoonotic coronavirus strain SARS-Cov2 was identified in patients with a rare and devastating Severe Acute Respiratory Syndrome or COVID19. Since the onset of the pandemic outbreak SARS-Cov2 virus has propagated rapidly across borders, jeopardizing the sanitary response of even the most advanced governments and economic blocks of the world to contain and fight the emergent disease. One of the most important challenges is the brevity and availability of the biological reagents required to test the presence of SARS-Cov2 for an expeditious and accurate diagnosis in equally clinically symptomatic and asymptomatic individuals. The current gold standard for the identification of SARS-Cov-2 is the RT-PCR reaction.

Tests provide crucial information for the identification, isolation and control of infected individuals, they offer invaluable information that helps to reduce the impact of the size of the outbreak and selectively limit the mobility of positively identified carriers, in order to minimize the contagion and reduce the workload of the healthcare personal, these measurements facilitate decisions takers estimate the initiation of early treatments that could lead to a satisfactory patient recovery. However, the cost of the enzymes and reagents represent a prohibitive expenditure for many hospitals and governments in developing nations or pose serious distribution obstacles for remote and inaccessible areas.

Materials and Method

Production Vector Construction

The plasmids contained pDawn, which was cloned when exposure to blue light activated the promoter inducing protein transcription and translation, and removal of the blue light halted the protein production, resulting in gene repression. Blue light was selected as the light source due to blue wavelengths’ narrow intensity peak that allowed for fine control of promoter activation. To facilitate column attachment and downstream processing, additions such as His tags were made to the plasmids. RFP served as the reporter for gene expression.

The plasmids were pDawn-Taq, pDawn-pfu-sso7d and pDawn-Mashup-RT. To clone these plasmids, the pDawn backbone was first linearized by PCR to generate overhangs necessary for TEDA assembly. The PCR reaction contained 1X Q5 Reaction Buffer, 1X GC Enhancer Buffer, 200 μM dNTPs, 0.5 μM pDawn-TEV-Vec-For primer, 0.5 μM pDawn-TEV-Vec-Rev primer, 0.5 ng pDawn-RFP plasmid, 1U Q5 DNA polymerase in a total volume of 25 μL. The PCR cycling conditions were as follows: initial denaturation at 95° C for 90s, 35 cycles of 95° C for 30s, 60° C for 30s, 72° C for 240s with a final extension of 72° C for 480s. Six reactions were pooled and treated with 20U of DpnI at 37° C for 2 hours. The PCR product was purified with a Biobasic PCR Purification kit and concentrated by vacuum centrifugation. Concentrated product was separated on a low-melt agarose gel and the 7.2 kb fragment was excised, purified with the Biobasic Gel Extraction kit and quantified by spectrophotometry. The Taq, pfu-sso7d and Mashup-RT inserts were purified as described above except that pAK-Taq, pET-28b-pfu-sso7d and pML-MashupRT plasmids were used as template with their respective primers. The assembly reaction contained 1X TEDA mix, 50 fmol of pDawn vector backbone and 150 fmol of insert in a total volume of 10 μL. The reaction was incubated at 30° C for 1 hour, and 1 μL was transformed into 100 μL DH5α competent cells. Colonies were screened for the correct insert by colony PCR with the same primers used to generate the inserts. The insert sequence was verified by plasmid isolation and Sanger sequencing.

~~The Gibson assembly procedure was used for vector construction from DNA fragments. The vector construction included maltose binding protein (MBP), TEV. proteinase and light inducible plasmids pDawn (ref). With pDawn, exposure to blue light activated the promoter inducing protein transcription and translation, and removal of the blue light halted the protein production, resulting in gene repression. Blue light was selected as the light source due to blue wavelengths’ narrow intensity peak that allowed for fine control of promoter activation. To facilitate column attachment and downstream processing, additions such as His tags were made to the plasmids. RFP served as the reporter for gene expression.~~

~~The DNA fragments were generated via PCR. Agarose gel was used to determine yield and purify the fragments. The fragments were then merged using T5 exonuclease to split the DNA ends to allow for the annealing of complementary fragments. Phusion DNA polymerase added the remaining base pairs, and Taq DNA ligase was inserted to unify the fragments into DNA molecules~~ ~~(4)~~~~. The plasmids were then used for bacterial transformation.~~

Growth Conditions
The bioreactor vessels are reusable silicone bags which, compared to glass containers, are less expensive since they do not require 3D printing of PP toxic filaments, are less fragile and are less bulky alternatives to glass jars.

A pump injects oxygen into the culture, which is approximately ⅓ the size of the bag. External agitation as a means of oxygen exposure, eliminates the need for shafts and propellers in the media and makes possible the growth of mammalian cells as shearing forces are less damaging. External agitation also enhances modularity, decreases the risk of leaks and simplifies the device layout and the autoclaving process. ___ was the sensor detecting oxygen transference rate (OTR), which served as a metabolic indicator of the rate at which the cells were absorbing oxygen.

The two environments used were 37°C at an optical density of 0.6, which requires a longer wait time than the other condition of room temperature and an optical density of 0.8 to 0.9.

An built in induction control system allows for production of several difficult enzyme classes like enzymes toxic to the host organism. Proteins from open sources or proteins that have an expired patent and other Open sources are cloned in the induction system.

Hardware Design

Motherboard

The sensor actuator system consists of an ESP 32 controller which operates a NEMA 17 stepper motor, and four peristaltic pumps. Advantages of the ESP 32 include Bluetooth and WiFi connectivity, a fast processor, and a large memory space.

An optional OLED display shows key parameters, including pH and temperature, and their values. A WiFi controller is used for communication between the display and the software.

Rocker

The rocker contains a lengthwise vertical beam supporting a baseplate and ball bearings mounted with laser-cut plates. The display rests on a moving component that slides out to a maximum of 10cm.

Motors control pH and pump air. Two heating pads control temperature. Sensors monitor cell media, temperature, pH, optical density. A set of 560-580 nm LEDs is used for protein induction detection.

Open Source Software

An Open Source JS library project is used for visualization of the data in real time. This allows for monitoring of the conditions inside the bioreactor in real time, either locally or remotely since the data from the run is transmitted over WiFi. The user can select which parameters to add to the line graph (shown on the left hand side of the screen), which displays how they change over time and how they compare to their target values. On the right hand side is a chart showing the real-time numerical values for each parameter, the parameter target values, and the current states of pumps and other devices controlling bioreactor conditions. The user also has the option to reset any of the controlled parameters to their default states.

The software also allows the user to compare multiple programs, each corresponding to a separate experiment, for the purpose of recording and analyzing past data. AI algorithms, trained on past data, determine how to optimize future experiments.

The software was developed in Eclipse.

Pre-existing software is used for temperature and OD600 determination.

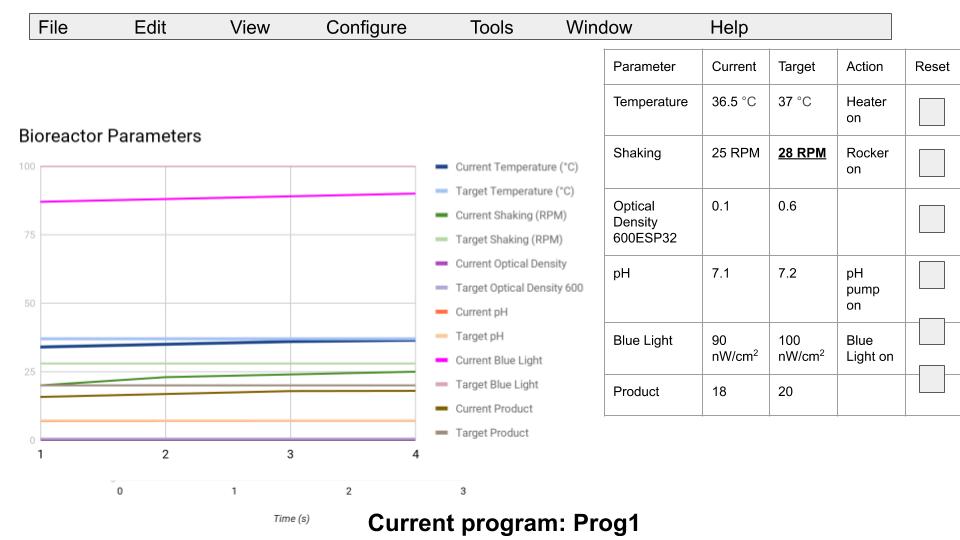
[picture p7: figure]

Method Validation

Results

- Efficiency in producing protein
- Silicon bag produced __ quantity of bacteria
- Software: you can watch from 3 screens
- Cost reductions: references #4, #51, #52
  - ~10x cheaper than average (see BOM)
  - Less than $200. Software used to keep cost down

Discussion

Design Implications

Implications of this bioreactor include the accessibility to a bioreactor that is extremely affordable compared to commercial ones. Anyone is free to follow the open source documentation and assemble the modular components into this bioreactor and use it to generate reagents. The access to a cheaply produced bioreactor enables the production of low-cost reagents, since making them is considerably less expensive than purchasing them. As a result, both the bioreactor and the reagents have a substantial return on investment. By reducing duces the impact of cost as an exclusionary factor to reagent production, our bioreactor contributes to the democratization of biotechnology, which is characterized by the increased popularity of do-it-yourself (DIY) designs that allow for the building of biotechnologies with affordable and readily available materials, which empowers many more people to experiment with (6 -- page 125, 127, 128). The presence of open source, low cost hardware and scientific equipment also has the effect of decreasing costs of commercial versions due to competition (1). With this bioreactor, researchers can create new tests or vaccines that can be used to detect or treat COVID-19, as well as other diseases. Since our design allows for the increased use of bioreactors, it also enables increased production of these tests, as well as cells, proteins, etc. with medical and research applications, that can then benefit a greater percentage of the general public.

Future Developments

Future iterations of this bioreactor could include further enhancements. Since the bioreactor is reusable, researchers can experiment with different variables in the controlled environments to discover how to optimize these reactions and create more effective reagents. The ESP 32 controller could be replaced with a larger processor to allow for more memory storage. Additional settings could be added to allow for the production of new types of reagents.

Since this bioreactor, as well as other open source designs, is publicly available on the Internet, there is an opportunity for collaboration among research groups. Researchers have the opportunity to offer feedback on and further expand upon these existing designs by incorporating their own ideas in order to further improve these devices (5). Since a remote team built this device, there is potential for future teams to assemble, regardless of location, to build upon the existing design.

Biorefinery and the future of Bioeconomy

Successful sustainable economies would likely depend on the migration from non-renewable fossil fuels into a rational use and production of renewable sources fuels and materials. In recent years the access to efficient, bioreactors are prohibitively expensive even for the

most technologically advanced economies. Nevertheless the opportunity to incorporate smaller, horizontal, low cost modular sources of biomolecules synthesis could facilitate the technological transference into diverse scales and levels of supply chains, representing an enormous cost reduction and overcoming distribution limitations. The advancement of open biorefinery production could be equiparable to additive manufacturing technologies (3D printing, laser cutting, material extrusion etc), where tools and machineries are designed in situ and on demand having a positive impact on the environmental footprint by the avoidance of cumulative, massively produced inventories.

References

1. https://www.ncbi.nlm.nih.gov/pubmed/22984059
2. https://github.com/
3. https://www.thingiverse.com
4. https://www.addgene.org/protocols/gibson-assembly/
5. https://journals.plos.org/plosone/article/file?type=printable&id=10.1371/journal.pone.0059840
6. https://app.slack.com/client/T010L5L681L/C010HURSND6/files/F0130LP3MBK

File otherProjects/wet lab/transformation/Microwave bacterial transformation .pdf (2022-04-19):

Glyxon Biolabs | Lab Protocols & Optimization | www.glyxonbiolabs.com

### Microwave Bacterial Transformation

This is a quick method for transformation of E. coli with plasmidic DNA.

Requirements:

a) Programable, household microwave oven.
b) Fridge with freezer.
c) Isolated plasmidic DNA (approx. 10ng for 100uL of cells are fine).
d) E.coli cell culture.
e) Autoclaved fresh LB media or 2xYT
(I leave the protocol for preparing it 2xYT in the addendum)
f) Autoclaved purified water.
g) Autoclaved plastic 1.5ml micro tubes (eppendorf), but you can use tall plastic 12cm capped tube if you have them.
h) Incubator, dry heat bath or a warm place around 37ºC where you can grow your cells.
i) Sterile, petri dish poured with LB media + selection antibiotics (check the resistance of your plasmids)
j) Plastic, glass or metal cell spreader, torch, bunsen burner, kitchen torch, alcohol lamp or if fancy enough, laminar flow hood.

The first step is check your microwave power output, check your original manual to estimate the maximum wattage output. According to it, you will have to adjust the output wattage between 150-180 to 300-340 watts approximately.

For example, my microwave maximum (100%) output is 800W, and I only have 5 options according to the power presets available in the programing menu: 100%, 80%, 60%, 40% and 20%. This means the power outputs can break down in the following way:

100% ————— 800W
80% ————— 640W
60% ————— 480W
40% ————— 320W
20% ————— 160W

Check your microwave if you have preset limits or if you can adjust power in a wider range or shorter intervals, but most of the time the low power output set will be required.

if you can’t reach out your manual or you don’t know the maximum output of your microwave unit, check this link and follow the instructions, so you can more or less estimate its wattage:

https://www.epicurious.com/expert-advice/how-to-find-adjust-wattage-power-of-microwaveoven-article

Glyxon Biolabs | Lab Protocols & Optimization | www.glyxonbiolabs.com

Once you know how to select the power of your microwave, let’s continue with the protocol:

1.- | Grown cell cultures to log phase (OD600 0.5) or early stationary phase (OD600 1.0)
2.- | Centrifuge them and resuspended in 1:1 LB/water and transferred to a clean sterile 1.5ml micro-tube in aliquots of 100uL.
3.- | Add the plasmid you want to transform (10ng per 100uL of cells)
4.- | Transfer you tube(s) to a cooler or plastic bag and place them in the freezer (-20ºC) for 1-3 minutes. Do not keep them in the freezer longer than 5mins.
5.- | Select power output of the microwave to 100W or 200W or a maximum of 300W (approx.) Place your tubes in the microwave, select time accordingly for 1minute (100W) or 30sec (300w) and press START
6.- | Take out your tubes and add up to 1ml of LB or 2xYT media, incubate 1hr at 37°C.
7.- | Plate your cells on the corresponding selective media (LB + agar + antibiotics), and controls, and incubate accordingly (37ºC or the suggested temperature, not all plasmids grow well at 37ºC, check the referred literature)

References:

You can read about the original methods from the following authors, this is a tested adaptation of the literature cited below:

R. Fregel et al, Letters in Applied Microbiology 46 (2008) 498–499

V.T. Tripp et al, J Chem Biol (2013) 6:135–140

Addendum:

2X YT Media Recipe (1000 ml)

1. Measure ~900ml of distilled H2O.
2. Add 16g Bacto Tryptone.
3. Add 10g Bacto Yeast Extract.
4. Add 5g NaCl.
5. Adjust pH to 7.0 with 5N NaOH.
6. Adjust to 1L with distilled H2O.
7. Sterilize by autoclaving.

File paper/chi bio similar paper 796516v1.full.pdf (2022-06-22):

## Chi.Bio: An open-source automated experimental platform for biological science research

Harrison Steel¹

, Robert Habgood¹
, Ciaran Kelly ´

2

, and Antonis Papachristodoulou¹

The precise characterisation and manipulation of in vivo biological systems is critical to their study.¹ However, in many experimental frameworks this is made challenging by non-static environments during cell growth,², 3 as well as variability introduced by manual sampling and measurement protocols.⁴ To address these challenges we present Chi.Bio, a parallelised open-source platform that offers a new experimental paradigm in which all measurement and control actions can be applied to a bulk culture in situ. In addition to continuous-culturing capabilities (turbidostat functionality, heating, stirring) it incorporates tunable light outputs of varying wavelengths and spectrometry. We demonstrate its application to studies of cell growth and biofilm formation, automated in silico control of optogenetic systems, and readout of multiple orthogonal fluorescent proteins. By combining capabilities from many laboratory tools into a single low-cost platform, Chi.Bio facilitates novel studies in synthetic, systems, and evolutionary biology, and broadens access to cutting-edge research capabilities.

Biology faces a crisis of reproducibility, caused in part by a lack of control over conditions experienced by cells prior to and during experiments.⁵ Biological systems are often characterised using batch-culture methods,⁶, 7 which make isolating a cellular sub-system’s behaviour from that of its host challenging.³, 8 To improve the robustness of biological data an ideal experimental setup would provide a controlled, static environment in which culture parameters such as nutrient availability and temperature are regulated,⁹
and
perform frequent and accurate measurements in situ. This can be partially achieved using continuous culture devices such as a Turbidostat, which dilutes cells during growth to maintain a constant optical density (OD). In recent years a number of Turbidostat platforms have been developed, and are beginning to find widespread applications in systems, synthetic, and evolutionary biology.¹⁰⁻¹⁵ However, in many cases these devices are not easy to build/obtain, require interfacing with external hardware (such as incubators), are inflexible for applications beyond their designed purpose, and lack in situ measurement and actuation capabilities (such as optogenetic actuation or measurement of fluorescent

1Department of Engineering Science, University of Oxford, Oxford, OX1 3PJ, UK. 2Department of Applied Sciences, Faculty of Health and Life Sciences, Northumbria University, Newcastle upon Tyne, NE1 8ST, UK. email: ({harrison.steel,antonis}@eng.ox.ac.uk). This research was supported by EPSRC project EP/M002454/1.

proteins) which are fundamental to many experimental studies.

To address these challenges we developed Chi.Bio,
a | parallelised | all-in-one | platform | for | automated
characterisation and manipulation of biological systems. It is open-source and can be built from printed circuit boards (PCBs) and off-the-shelf components for ∼ $300 per device. The platform comprises three primary components (Fig. 1a); a control computer, main reactor, and pump board. The control computer can interface with up to eight reactor/pump pairs in parallel, allowing independent experiments to be run on each. It also hosts the platform’s operating system, which provides an easy-to-use web interface for real-time control and monitoring of ongoing experiments. The main reactor contains most of the platform’s measurement and actuation sub-systems (Fig. 1b), which operate on standard 30 mL flat-bottom screw-top laboratory test tubes (with a 12 to 25 mL working volume). All measurement and actuation systems (with the exception of the heat plate) are non-contact, minimising sterilisation challenges and allowing test tubes to be hot swapped during operation. Each reactor can accept up to four liquid in/outflow tubes, which are driven by peristaltic pumps housed in the reactor’s dedicated pump board. The platform as a whole is entirely modular (the three components inter-connect via micro-USB cables), allowing it to be tailored to a wide variety of experimental configurations.

Experimental techniques which exploit interactions between light and life, such as light-sensitive proteins, optogenetics, and fluorescent reporters, are ubiquitous in biological research.¹⁶, 17 Chi.Bio contains an array of optical outputs and sensors to support these techniques (Fig. 2a). A 650nm laser is used for optical density measurement (calibrated against a Spectrophotometer, Note S5), and is driven by an analogue feedback circuit (Fig. S6) to provide stable, temperature-insensitive readings (Note S6). Optogenetic actuation and excitation of fluorescent proteins employs a focused high-power 7-Colour LED with six emission bands across the visible range and a 6500K white output (Fig. 2b,c), and a separate 280nm UV LED is included to stress/sterilise cells. Each LED has an independent current-limiting pulse width modulation (PWM) driver (Fig. S6), allowing its intensity to be regulated over three orders of magnitude (Fig. S7), and is thermally coupled to the outside of the device to reject heat when operating at high intensity. The combined LED implementation provides certified by peer review) is the author/funder. All rights reserved. No reuse allowed without permission.

bioRxiv preprint doi: https://doi.org/10.1101/796516; this version posted October 7, 2019. The copyright holder for this preprint (which was not

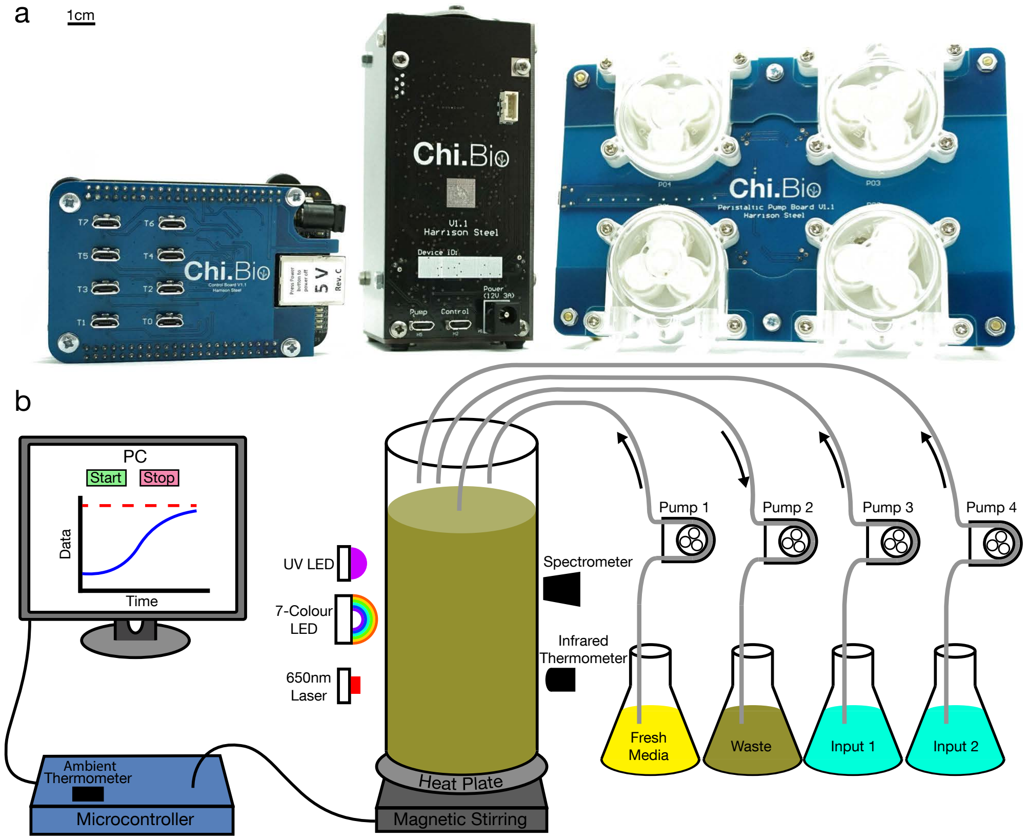
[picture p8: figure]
Data; Time; Start; Stop; Microcontroller; Magnetic Stirring; Spectrometer; Infrared Thermometer; 7-Colour LED; UV LED; 650nm Laser; Pump 1; Pump 2; Pump 3; Pump 4; Ambient Thermometer; Fresh; Media; Waste; Input 1; Input 2

Fig. 1: (a) The Chi.Bio platform comprises a control computer (left), main reactor (centre), and peristaltic pump board (right). The system is open-source and can be constructed for ∼ $300 using only PCBs and off-the-shelf components. Scale bar indicates 1 cm, giving the main reactor dimensions of 11.5×5.3×5.3 cm. (b) Schematic of sub-systems and interconnections. A lab computer or network connects to the control computer, which runs the platform’s operating system and can interface with up to eight reactor/pump pairs in parallel. Each reactor has a 12 to 25 mL working volume and contains a range of measurement and actuation tools for precise in situ manipulation of biological systems. These include a UV LED, a 650nm laser (for OD measurement), seven coloured LEDs in the visible range (for optogenetics and fluorescence measurement), and a spectrometer. An infrared thermometer and heat plate are used to regulate temperature, and the culture is agitated using magnetic stirring. Each reactor has a modular pump board with four direction- and speed-controllable peristaltic pumps. For a detailed descriptions of each hardware sub-system see Notes S1-S4.

optical outputs that exhibit minimal power and spectral variability between devices or environmental conditions (Note S7).

Measurements of light intensity are performed within the device by a chip-based spectrometer with eight optical filters covering the visual range, as well as an un-filtered “Clear” sensor (Fig. 2d). Multiple wavelength bands can be measured simultaneously, each with electronically adjustable gain and integration time. The spectrometer is set up to perform temperature and long-term baseline calibration using a dark photodiode prior to every measurement. Typical spectrometer measurements (e.g. of fluorescence) are reported as the ratio of light intensity measured at the fluorescent protein’s emission band to the total intensity of the excitation source; this ratiometric measurement mitigates the impact of differing excitation intensity between devices and spatial variations in culture density.

Culture temperature is measured non-invasively by a medical-grade infrared thermometer, which is accurate to ± 0.2 ◦C for temperatures near 37 ◦C. There are also Air temperature thermometers (± 0.5 ◦C accuracy) within the main reactor and on the control computer for monitoring the surrounding environment. Temperature change is actuated by a PCB-based heat plate, capable of heating a 20 mL culture at up to 2.0 ◦C min⁻¹
. Below the heat plate is a magnetic stirring assembly built upon an off-the-shelf fan, which has an adjustable stirring rate (Fig. 2e) and can be used with standard laboratory stir bars. The main reactor also includes an external expansion port, which provides power and a digital interface for user-built add-ons to Chi.Bio.

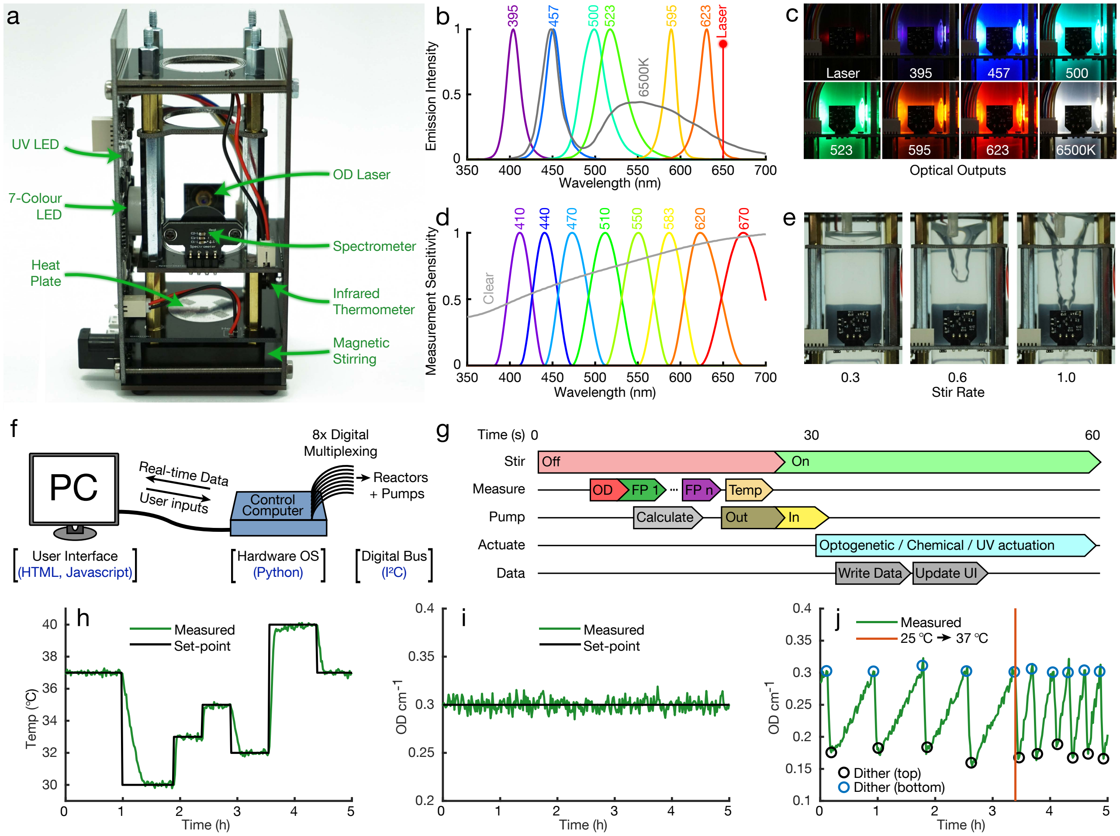
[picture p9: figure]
UV LED; 7-Colour LED; Heat Plate; Magnetic Stirring; Spectrometer; OD Laser; Infrared Thermometer; Wavelength (nm); Emission Intensity; Measurement Sensitivity; Clear; 623 Laser; Laser; Stir; Pump; Time (s); Measure; Data; Off; Out; Calculate; Write Data Update UI; Time (h); Temp (; Measured Set-point; Measured; Dither (top) Dither (bottom); Stir Rate; Optical Outputs; FP n Temp; 8x Digital Multiplexing; Reactors + Pumps Control Computer; Hardware OS (Python); User Interface [(HTML, Javascript) [; Digital Bus [; (I²C) [ [; Real-time Data; User inputs

Actuate | Optogenetic / Chemical / UV actuation

Fig. 2: Hardware sub-systems, software, and automation. (a) The main reactor with sides removed and sub-systems labelled. The vertical PCB on the left hosts driving circuitry for many sub-systems, as well as power regulation and filtering. (b) Emission spectra of the optical outputs in the device (280nm UV LED not shown). (c) Images of optical outputs, with laser set to 50% and LEDs to 5% intensity. LEDs are focused and perpendicular to the spectrometer to maximise faint fluorescence signals. (d) Measurement filter bands of the platform’s spectrometer. (e) Magnetic stirring provides a powerful vortex when set to a high rate. (f) Software architecture, which packages multiplexed low-level commands (digital communications following I²C standard) into an easy-to-use web interface accessed from a connected PC or network. (g) A typical 60 second experimental automation cycle. Initially stirring is disabled so liquid can settle, reducing noise in measurements and providing a flat surface for removal of waste media. (h) Media temperature controlled to follow a pre-defined path over 5 hours. Heat input is provided by the heat-plate, cooling is passive. (i) The OD of E. coli in exponential growth phase, maintained within ∼ 2% of its set-point. (j) OD can be set to follow a dithered waveform (with cells rapidly diluted to a lower OD value whenever the upper limit is reached) to accurately measure growth.¹⁸ Following a change in temperature set-point from 25 ◦C to 37 ◦C growth accelerates significantly.

External to the main reactor is a pump board, which can house up to four low-cost peristaltic pumps with independently controllable speed (up to 1 mL s⁻¹
) and
direction. Each pump transfers liquid to/from the culture test tube via standard 4.5mm silicone laboratory tubing, which can be installed without joints from input to output to assist sterilisation. Typically two pumps are dedicated to turbidostat functionality (one for input of fresh media, one for removal of waste), leaving the other two free for programmable mixing of media/inducers, or transfer of liquid between reactors. Detailed specifications of Chi.Bio’s hardware and electrical sub-systems are outlined in Notes S1-S4, and analysis of their calibration, measurement stability, and inter-device variability is described in Notes S5-S7.

At the lowest level of Chi.Bio’s open-source operating system is a multiplexed I²C bus for digital communications within the device (Fig. 2f). Digital signals are in turn controlled by the hardware operating system (Python, Note

Time (h)

OD cm-1

Temp ( °C)

0

0.5

1

1.5

2

2.5

3

Growth Rate (h-1)

Time (h)

-0.1

0

0.1

0.2

0.3

0.4

0.5

Biofilm OD cm-1

WT
Adapted

Time (h)

0

0.5

1

1.5

2

2.5
Growth Rate (h-1)
25 | 30 | 35 | 40 | 0 | 2 | 4 | 6 | 8 | 0 | 10 | 20 | 30 | 40 UV on

0.1

0.03
0.01

0.005

0

0 | 10 | 20 | 30
Time (h)

0

0.02

0.04

0.06

Fluorescence (GFP) (a.u.)

0 | 2 | 4 | 6 | 8 | 10 12
| | | Time (h)

0

0.01

0.02

0.03

0.04
Fluorescence (GFP) (a.u.)
0 | 10 | 20 | 30
| | Time (h)

0

0.005

0.01

0.015

0.02
Fluorescence (GFP) (a.u.)

0

0.1

0.2

0.3

525nm Excitation Intensity

Measured
OL set-point

Time (h)

0

0.01

0.02

0.03

0.04
Fluorescence (GFP) (a.u.)

Measured
CL set-point
0 | 10 | 20 | 30 | 40
e | f | g | h
| | Application 2 - Optogenetic In Silico Control

Application 3 - Multiple Fluorescent Outputs

Application 1 - Studying Growth
a | b | d c

0

1

2

3

4

0 | 5 | 10

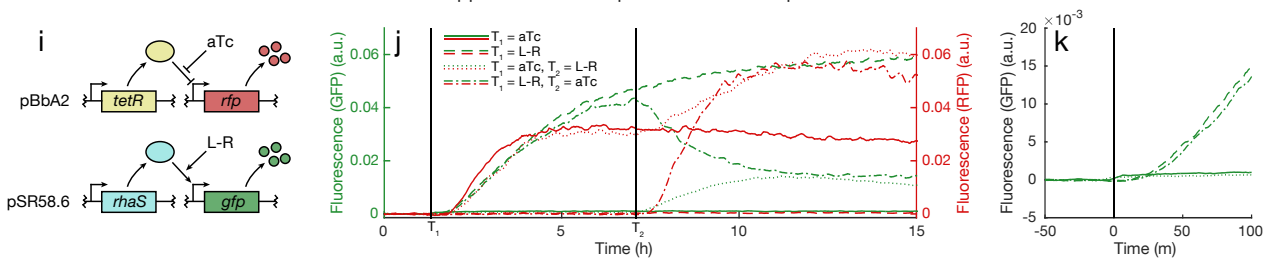
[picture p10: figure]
Time (m); Fluorescence (GFP) (a.u.); Time (h); Fluorescence (RFP) (a.u.); = aTc; = aTc, T2; tetR; rfp; aTc; rhaS; gfp; pBbA2; pSR58.6

Fig. 3: Application 1 - (a) Growth curves of E. coli (four replicates). (b) Dependence of E. coli growth rate on temperature, error bars represent standard deviation of growth rates measured over five hours at each temperature. (c) Measured growth rate following activation of UV source at specified power level at t = 1 hour. The population is able to adapt to low UV intensities and eventually returns to its initial growth rate (Fig. S23). (d) Biofilm optical density versus time for cells before and after adaptation in Chemostat mode for 120 hours, calculated as described in Note S14. Application 2 - (e,f) Optogenetic CcaS-CcaR system coupled to GFP expression,¹⁹ stimulated with slow- and fast-varying inputs (green/red light activate/deactivate gene expression respectively). (g) Fluorescence expression (left axis) controlled by varying optogenetic excitation intensity (right axis) in open loop (OL). (h) Fluorescence expression regulated in closed loop (CL) to follow a pre-determined profile, using a proportional-integral (PI) controller. Application 3 - (i) Two-plasmid system for inducible expression of GFP and RFP. (j) Fluorescence of GFP (left axis) and RFP (right axis) following induction at times T1 and T2 with indicated inducer combinations. (k) GFP fluorescence measured during short time period near T1. A small increase is observed in the two samples to which aTc is added due to the fluorescence of the inducer compound itself.

S8), which implements automation functions as well as data
collection, processing, and storage (in .csv format). Real-time data is output periodically via a web-server (accessible from a connected PC or network) which provides an easyto-use web user interface (built in HTML/Javascript, Note S9). The complete software stack lets users set up, control, and monitor standard experiments entirely through their web browser, and more advanced protocols or algorithms which combine any of the platform’s measurement/actuation capabilities can be easily implemented using the in-built “custom program” Python framework (Note S10).

A typical automated experiment follows a 60 second cycle (Fig. 2g) during which the stirring vortex is allowed to settle prior to measurement, media/waste is added/removed, and data is processed to calculate new control inputs. This automation protocol can be adjusted in real-time to change controller set-points or measurement setup, all of which are recorded throughout an experiment. Automated temperature and OD regulation are implemented using PID and Model Predictive Control (MPC) algorithms.²⁰ The temperature control algorithm (Note S11) facilitates rapid temperature changes with minimal error and set-point overshoot (Fig. 2h). The OD control algorithm (Note S12) typically maintains OD within ∼2% of its set-point (Fig. 2i), and can also be used to dither a culture’s OD about a central set-point (Fig. 2j) for precise measurement of growth rate at near-constant density.¹⁸

A straightforward application of Chi.Bio is the study and regulation of growth in changing conditions. This can involve the collection of growth curves (Fig. 3a), or dithering of OD near a set-point (as in Fig. 2j) to analyse the dependence of growth on a particular parameter (e.g. temperature, Fig. 3b). The UV output can be used to stress cells (or encourage mutagenesis²¹); in Fig. 3c E. coli is subjected to different UV intensities, causing a gradual reduction in growth. Chi.Bio can also be used to monitor the growth of biofilms (using the procedure outlined in Note S14); in Fig. 3d we observe that initial adaptation to the continuous culture environment (which actively selects for biofilm-forming phenotypes²²) leads to accelerated biofilm formation.

Real-time interfacing between in silico computational elements and biological systems can facilitate novel studies²³ and optimise experimental schemes.²⁴ We implemented such a scheme as a “custom program” in the platform, which uses the red (623nm) and green (523nm) LEDs as actuating inputs for the CcaS-CcaR optogenetic system coupled to GFP expression.¹⁹ In Figs. 3e,f this system is probed with square wave inputs of varying frequency, which yield smoothed output signals (due to the dynamics of protein expression/maturation). In Fig. 3g an input of varying intensity is supplied, revealing a non-linear dependence between fold-change of input versus output. This highlights a major challenge posed by open-loop control of biology; predicting a priori the behaviour of such complex, non-linear systems requires accurate and implementation-specific models,⁶, 25 which may only be relevant in a limited range of tightly controlled environmental conditions. This can be overcome by in silico feedback control:¹² In Fig. 3h our custom program implements a control law which updates the optogenetic excitation intensity each minute depending on the measured fluorescence, steering the culture’s fluorescence to follow a complex profile without requiring a model or extensive a priori analysis of the biological system itself.

Characterisation of biological systems often requires
monitoring | of | multiple | fluorescent | protein-tagged
outputs.⁷, 26, 27 | Here we demonstrate the effectiveness
of Chi.Bio for probing such a system (Fig. 3i). Adding chemical inducers in different orders highlights the impact that cellular burden⁷ has on its two outputs (Fig. 3j): if RFP is induced after GFP we observe a significant drop in GFP (due to limited resource availability for production of GFP and its activating transcription factor RhaS). However, if RFP is induced first the subsequent induction of GFP leads to an increase in RFP expression, which we hypothesise is due to the effect of resource limitation on expression of its repressing transcription factor TetR (repeatability of this behaviour is illustrated in Fig. S28). In all cases we observe negligible cross-talk between fluorescent protein measurement channels, and our instrument’s high sensitivity allows fluorescence activation to be observed within ∼ 20 minutes of induction (Fig. 3k, approximately the time required for fluorophore maturation).

The applications outlined herein represent only a fraction of Chi.Bio’s potential use-cases. The platform’s turbidostat functionality lends its application to continuous directed evolution²⁸ (as demonstrated by eVOLVER¹³) which could be tuned using the UV output.²¹ Direct integration of fluorescence measurement with chemical/optogenetic actuation and computational capabilities facilitates optimised experimental design²⁵ and the implementation of online experimental-planning algorithms.²⁴ Given that the only components of Chi.Bio which come into direct contact with cells are standard laboratory consumables (glass test tubes, silicone tubing, magnetic stir bars), such experiments could be run with a broad range of cell types and reagents (e.g. algae, with photosynthesis supported by the tunable LED outputs). A list of potential applications (and minor hardware modifications that can be made to enable others) is presented in Table S1.

The cost and resulting inaccessibility of modern scientific hardware is one of the primary obstacles to participation in cutting-edge research worldwide, particularly in small laboratories and institutions or developing nations.²⁹ Consequently we have made Chi.Bio entirely open-source, with schematics, code repositories, user manuals, and a public support and discussion forum all available on the project’s website (https://chi.bio). A single Chi.Bio device (consisting of one control computer, one reactor, and one pump board) can be assembled by hand for ∼ 300, or can be purchased ready-built from a supplier of open-source scientific hardware. In the long term we hope that Chi.Bio will provide a versatile tool for biological sciences, and broaden access to cutting-edge research capabilities.

ACKNOWLEDGEMENTS

The authors would like to thank Prof Wei Huang for use of his laboratory space.

AUTHOR CONTRIBUTIONS

H.S. conceived the study and performed all hardware and software engineering. R.H., H.S., and C.K. planned and conducted biological characterisation experiments. All authors wrote the manuscript.

COMPETING INTERESTS

The authors declare no competing interests.

REFERENCES

[1] B. Canton, A. Labno, and D. Endy, “Refinement and standardization of synthetic biological parts and devices,” Nature Biotechnology, vol. 26, no. 7, pp. 787–793, 2008.
[2] J. Monod, “The Growth of Bacterial Cultures,” Annu. Rev. Microbiol, vol. 3, pp. 371–394, 1949.

[3] M. Scott, C. W. Gunderson, E. M. Mateescu, Z. Zhang, and T. Hwa, “Interdependence of Cell Growth,” Science, vol. 330, no. 6007, pp. 1099–1102, 2010.
[4] J. Beal, T. Haddock-Angelli, M. Gershater, K. de Mora, M. Lizarazo,
J. Hollenhorst, R. Rettberg, and iGEM Interlab Study Contributors, “Reproducibility of Fluorescent Expression from Engineered Biological Constructs in E . coli,” PLoS ONE, vol. 11, no. 3, pp. 1–22, 2016.
[5] M. M. Jessop-Fabre and N. Sonnenschein, “Improving Reproducibility in Synthetic Biology,” Frontiers in Bioengineering and Biotechnology, vol. 7, no. February, pp. 1–6, 2019.
[6] E. J. Olson, L. A. Hartsough, B. P. Landry, R. Shroff, and J. J. Tabor, “Characterizing bacterial gene circuit dynamics with optically programmed gene expression signals.” Nature methods, vol. 11, no. 4, pp. 449–55, 2014.
[7] A. Gyorgy, J. I. Jimenez, J. Yazbek, H. H. Huang, H. Chung, R. Weiss, ´ and D. Del Vecchio, “Isocost Lines Describe the Cellular Economy of Genetic Circuits,” Biophysical Journal, vol. 109, no. 3, pp. 639–646, 2015.
[8] K. Valgepea, K. Adamberg, A. Seiman, and R. Vilu, “Escherichia coli achieves faster growth by increasing catalytic and translation rates of proteins,” Molecular BioSystems, vol. 9, no. 9, pp. 2344–2358, 2013.
[9] R. Portner, O. Barradas, B. Frahm, and V. Hass, “Advanced Process ¨ and Control Strategies for Bioreactors,” in Current Developments in Biotechnology and Bioengineering, C. Larroche, M. Sanroman, G. Du, ´ and A. Pandey, Eds., 2017, pp. 463–493.
[10] E. Toprak, A. Veres, S. Yildiz, J. M. Pedraza, R. Chait, J. Paulsson, and R. Kishony, “Building a morbidostat: An automated continuous-culture device for studying bacterial drug resistance under dynamically sustained drug inhibition,” Nature Protocols, vol. 8, no. 3, pp. 555– 567, 2013.
[11] C. N. Takahashi, A. W. Miller, F. Ekness, M. J. Dunham, and
E. Klavins, “A low cost, customizable turbidostat for use in synthetic circuit characterization,” ACS Synthetic Biology, vol. 4, no. 1, pp. 32– 38, 2015.
[12] A. Milias-Argeitis, M. Rullan, S. K. Aoki, P. Buchmann, and
M. Khammash, “Automated optogenetic feedback control for precise and robust regulation of gene expression and cell growth,” Nature Communications, vol. 7, no. May, p. 12546, 2016.
[13] B. G. Wong, C. P. Mancuso, S. Kiriakov, C. J. Bashor, and A. S. Khalil, “Precise, automated control of conditions for high-throughput growth of yeast and bacteria with eVOLVER,” Nature Biotechnology, vol. 36, no. 7, pp. 614–623, 2018.
[14] A. M. McGeachy, Z. A. Meacham, and N. T. Ingolia, “An Accessible Continuous-Culture Turbidostat for Pooled Analysis of Complex Libraries,” ACS Synthetic Biology, vol. 8, no. 4, pp. 844–856, 2019.
[15] D. Bergenholm, G. Liu, D. Hansson, and J. Nielsen, “Construction of mini-chemostats for high-throughput strain characterization,” Biotechnology and Bioengineering, vol. 116, no. 5, pp. 1029–1038, 2019.
[16] E. A. Rodriguez, R. E. Campbell, J. Y. Lin, M. Z. Lin, A. Miyawaki,
A. E. Palmer, X. Shu, J. Zhang, and R. Y. Tsien, “The Growing and Glowing Toolbox of Fluorescent and Photoactive Proteins,” Trends in Biochemical Sciences, vol. 42, no. 2, pp. 111–129, 2017.
[17] Z. Liu, J. Zhang, J. Jin, Z. Geng, Q. Qi, and Q. Liang, “Programming bacteria with light-sensors and applications in synthetic biology,” Frontiers in Microbiology, vol. 9, no. NOV, 2018.
[18] S. A. Hoffmann, C. Wohltat, K. M. Muller, and K. M. Arndt, “A ¨ user-friendly, low-cost turbidostat with versatile growth rate estimation based on an extended Kalman filter,” PLoS ONE, vol. 12, no. 7, pp. 1–15, 2017.
[19] N. T. Ong and J. J. Tabor, “A Miniaturized Escherichia coli Green Light Sensor with High Dynamic Range,” ChemBioChem, vol. 19, no. 12, pp. 1255–1258, 2018.
[20] R. C. Dorf and R. H. Bishop, Modern Control System, 12th ed. Pearson, 2011.
[21] A. Shibai, Y. Takahashi, Y. Ishizawa, D. Motooka, and S. Nakamura, “Mutation accumulation under UV radiation in Escherichia coli,” Scientific Reports, no. July, pp. 1–12, 2017.
[22] J. D. Bryers, “Biofilm Formation and Chemostat Dynamics : Pure and Mixed Culture Considerations,” Biotechnology and Bioengineering, vol. 26, pp. 948–958, 1984.
[23] A. Milias-Argeitis, S. Summers, J. Stewart-Ornstein, I. Zuleta, D. Pincus, H. El-Samad, M. Khammash, and J. Lygeros, “In silico feedback for in vivo regulation of a gene expression circuit.” Nature biotechnology, vol. 29, no. 12, pp. 1114–6, 2011.
[24] L. Bandiera, Z. Hou, V. B. Kothamachu, E. Balsa-Canto, P. S. Swain, and F. Menolascina, “On-line optimal input design increases the efficiency and accuracy of the modelling of an inducible synthetic promoter,” Processes, vol. 6, no. 9, 2018.
[25] J. Ruess, F. Parise, A. Milias-Argeitis, M. Khammash, and J. Lygeros, “Iterative experiment design guides the characterization of a lightinducible gene expression circuit,” Proceedings of the National Academy of Sciences of the United States of America, vol. 112, no. 26, pp. 8148–8153, 2015.
[26] L. Potvin-Trottier, N. D. Lord, G. Vinnicombe, and J. Paulsson, “Synchronous long-term oscillations in a synthetic gene circuit,” Nature, vol. 538, no. 7626, pp. 514–517, 2016.
[27] H.-H. Huang, Y. Qian, and D. D. Vecchio, “A quasi-integral controller for adaptation of genetic modules to variable ribosome demand,” Nature Communications, vol. 9, no. 5415, 2018.
[28] S. D’Oelsnitz and A. Ellington, “Continuous directed evolution for strain and protein engineering,” Current Opinion in Biotechnology, vol. 53, pp. 158–163, 2018.
[29] A. Maia Chagas, “Haves and have nots must find a better way: The case for open scientific hardware,” PLoS biology, vol. 16, no. 9, p. e3000014, 2018.

METHODS

Strain and plasmid selection. Escherichia coli strain MG1655 was used for growth/biofilm characterisation experiments. Fluorescent protein experiments utilised BL21(DE3) E. coli, apart from the optogenetics experiments which utilised BW29655. Bacterial strains were made chemically competent by treatment with calcium chloride and transformations were performed via heat shock. All E. coli strains used in this study are freely available (Table S2), as are plasmids (Table S3).

Culture techniques. Cells were cultured in either LB (growth/biofilm experiments), or EZ rich defined media (Teknova Inc; cat: M2105) supplemented with 1% (v/v) glycerol (for optogenetic/fluorescence experiments). All experiments were performed in 20 mL volume in 30 mL test tubes (Fisher Scientific, 11593532) open to atmosphere. Stirring employed disk stir bars (Fisher Scientific, 11878892) at speed setting 0.6. Culture temperature was maintained at 37◦C unless otherwise stated. For fluorescent protein and optogenetic experiments cells were maintained at an OD of
0.4. Carbenicillin (a semi-synthetic analogue of ampicillin with greater stability), chloramphenicol, and spectinomycin were used at final concentrations of 100 µg mL⁻¹
, 25 µg
mL⁻¹

, and 50 µg mL⁻¹
, respectively.

Experiment setup procedure. Prior to experiments test tubes and stir bars were sterilized by autoclave. Silicone tubing was sterilised by pumping 70% ethanol for 10 seconds, and media for 5 seconds. For experiments that required chemical induction (Application 3) an additional 500 mL of tap water was pumped through each tube prior to the experiment to prevent inducer cross-contamination. Tubing exterior was sterilised via swabbing with 70% ethanol. For each media type, each reactor’s OD zero point was calibrated with a test tube of fresh media as described in Note S5. Test tubes were filled with 20 mL media and inoculated prior to insertion into each reactor.

Biofilm experiments. In each trial cells were initially diluted to an OD of 0.1, and (once reached) maintained at an OD of 0.5. Each experiment’s zero-time is defined as the time when the culture first reached OD 0.5 (typically ∼ 2 hours post-inoculation). To develop a biofilm forming phenotype E. coli was grown at high density (OD > 1) in LB media in a reactor in chemostat mode for 120 hours. Samples from this culture were subsequently used to inoculate each of the “adapted” biofilm trials.

Fluorescence measurements. GFP was excited by the 457nm LED at power setting 0.1, and measured at x512 gain and 0.7s integration time using the Clear filter as base-band and 550nm filter as emission band. RFP was excited by the 595nm LED at power setting 0.1, and measured at x512 gain and 0.7s integration time using the Clear filter as base-band and 670nm filter as emission band. A baseline fluorescence (corresponding to the fluorescence measured for wild-type cells without plasmid) was subtracted from each measurement. Measurements were then smoothed using a moving mean filter with 10 minute width. Examples of raw (unprocessed) data are presented in Fig. S27. For a detailed analysis of the fluorescence measurement procedure see Note S15.

Optogenetic control. In optogenetic experiments which required full activation/deactivation (Fig. 3e,f) either the green (525nm) or red (625nm) LED was enabled individually at power setting 0.1. In experiments where the precise induction level was controlled (Fig. 3g,h) the procedure suggested by Olson et al.⁶ was followed; the red LED was illuminated at a fixed power setting of 0.1, and the green LED’s intensity was varied.

Chemically | induced | reporters. | In | fluorescence
experiments which used chemically-inducible fluorescent reporters L-Rhamnose concentrations of 0.1 mg mL⁻¹
| | | | and
aTc concentrations of 300 nM were used. At the time of induction each inducer was added manually to both the reaction chamber and the fresh media supply (to provide a sharp step-increase) without stopping the experiment.

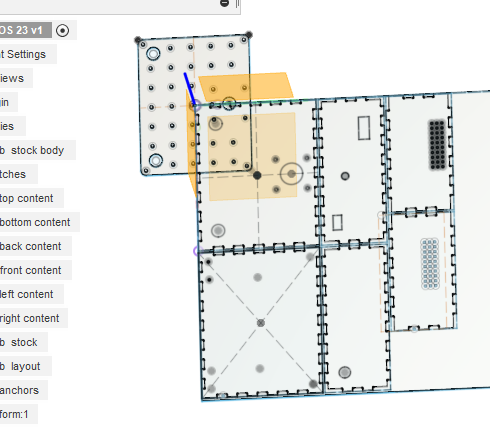
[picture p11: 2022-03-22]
otherProjects/orbital shaker and incubator/cooling shaker for David/mechanical/box from scriptOS Fusion360 file below.png

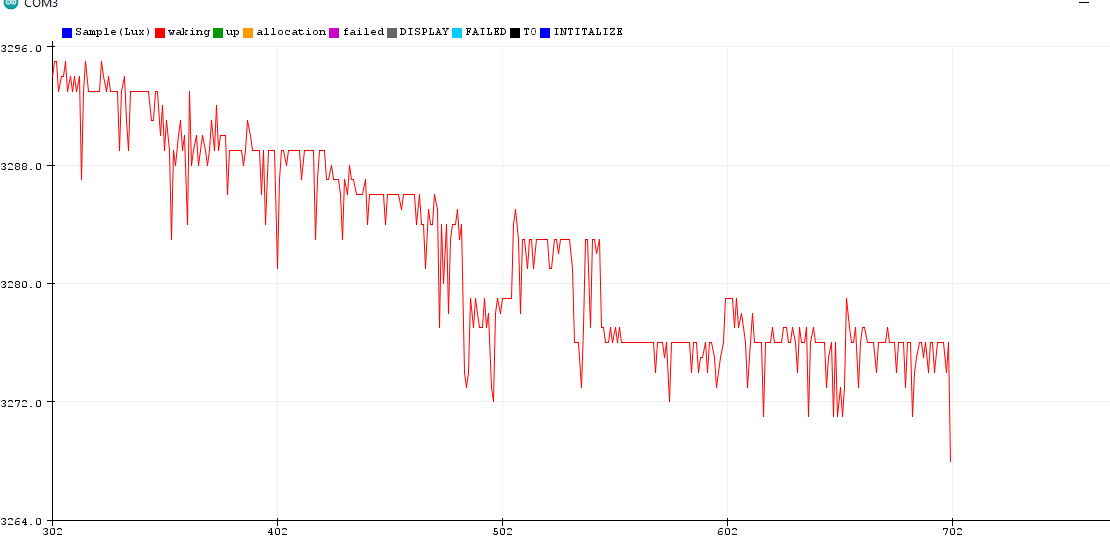
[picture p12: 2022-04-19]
otherProjects/opticalDensity/2 minute graph of sample light in Lux.png

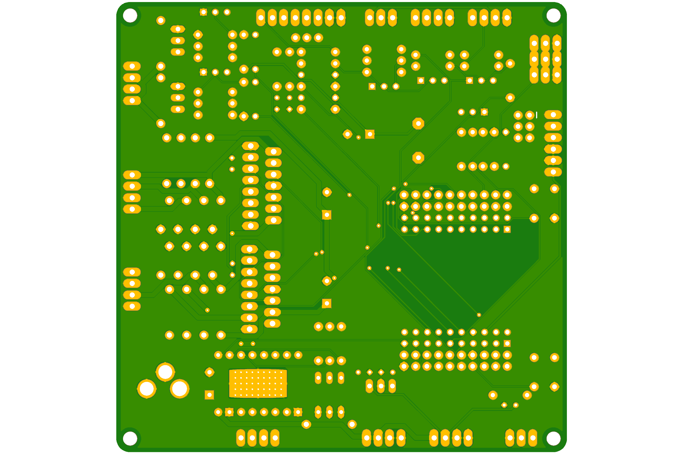
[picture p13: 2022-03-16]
electronics/eagle files/ESP32_BioReactor_v1_Original first board/ESP32_BioReactor_v1_bot.png

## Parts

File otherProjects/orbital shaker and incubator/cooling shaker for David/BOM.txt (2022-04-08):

main board:
https://www.aliexpress.com/item/1005003287023654.html?spm=a2g0o.order_list.0.0.21ef1802SkMBOH  the thid one Color: DLC32-8825
--------------
driver for the Peltier
https://www.aliexpress.com/item/4000559513023.html?spm=a2g0o.productlist.0.0.61202626Wmiq0q&algo_pvid=fa94df9c-3ac4-465d-88f0-ffd533cb69d6&algo_exp_id=fa94df9c-3ac4-465d-88f0-ffd533cb69d6-0&pdp_ext_f=%7B%22sku_id%22%3A%2210000002935273562%22%7D&pdp_pi=-1%3B1.8%3B-1%3B-1%40salePrice%3BCAD%3Bsearch-mainSearch
--------------
mounting pieces for PCBs
https://www.aliexpress.com/item/33054086915.html?spm=a2g0o.order_list.0.0.21ef1802Fz4SFG-
White, M2.5 50PCS, 5mm
----------
screws and nuts for links:
https://www.aliexpress.com/item/1005002998515190.html?spm=a2g0o.order_list.0.0.21ef18024V1Oa0 OpenBuilds Low Profile -screws M5 M5, 20mmx30pcs
https://www.aliexpress.com/item/32798773566.html?spm=a2g0o.order_list.0.0.21ef18024V1Oa0    black carbon steel, 25pcs M5
wires:
https://www.aliexpress.com/item/32481623557.html?spm=a2g0o.order_list.0.0.21ef18029GRQrz, Color: 20cm 3 kinds
----------
screws for NEMA mounting
THIS ONE IS CORRECT: 
 -M3 50pcs, 12mm 
or maybe M3 (50PCS), 10mm I don't remember  The depts inside Nema is 4.5 mm, the HDPE is about 3.1 mm
------------
NEMA 17
https://www.aliexpress.com/item/32604862242.html?spm=a2g0o.order_list.0.0.21ef1802f2fy5R, you might want to buy a stronger NEMA 17 so please look for it
------------
Power adapter: use the one for the Bioreactor. The voltage should be not lower than 12 volts. The Bioreactor  is 19.5 volts and 4.75 Amps
-----------

5 Flanged Ball Bearings. Sasha ordered them. The looked like https://www.aliexpress.com/item/32969902506.html?spm=a2g0o.productlist.0.0.721a503d45a7vz&algo_pvid=ed46f52d-4c3f-4166-b2b4-2cab34443152&algo_exp_id=ed46f52d-4c3f-4166-b2b4-2cab34443152-2&pdp_ext_f=%7B%22sku_id%22%3A%2266625097318%22%7D&pdp_pi=-1%3B4.47%3B-1%3B-1%40salePrice%3BCAD%3Bsearch-mainSearch
Ours are 6mm for the hole, medium diam is 13 mm,height is 5 mm including 1 mm lip and flange diam is 15mm. Please ask Sasha for the exact details

---------
one fan for general air circulation
https://www.aliexpress.com/item/32373802890.html?spm=a2g0o.productlist.0.0.48bb25e3ynAQ0y&algo_pvid=16e259e8-6a30-47dc-b321-56a7f30c6fb5&algo_exp_id=16e259e8-6a30-47dc-b321-56a7f30c6fb5-0&pdp_ext_f=%7B%22sku_id%22%3A%2210000000693005613%22%7D&pdp_pi=-1%3B4.45%3B-1%3B-1%40salePrice%3BCAD%3Bsearch-mainSearch get the 24 volt if your power is >12 volts
-----
We still need the details for the Peltier and decide if it should come with thermal sink and fan. The iggest watts or Amps the cooler and it should match the ma Wattage and Amps for the driver for the Peltier. Maybe something like https://www.aliexpress.com/item/1005003762477670.html?spm=a2g0o.productlist.0.0.21535d3bgdQhgY&algo_pvid=41b4aed3-1eeb-4210-8bbb-f16a89ca994c&algo_exp_id=41b4aed3-1eeb-4210-8bbb-f16a89ca994c-57&pdp_ext_f=%7B%22sku_id%22%3A%2212000027080528075%22%7D&pdp_pi=-1%3B22.18%3B-1%3B-1%40salePrice%3BCAD%3Bsearch-mainSearch

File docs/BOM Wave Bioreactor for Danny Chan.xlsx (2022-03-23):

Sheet: Sheet1
Documentation | Price (min) C$ | Name | Qty | Buy | Buy Alt1 | Buy Alt2 |  | Part No./Material
 | 7 | Controller ESP32 | 1 | amazon com (https://www.amazon.com/WINGONEER-Esp32-Module-Bluetooth-Esp32-Wrover/dp/B07RW311YR) | amazon ca (https://www.amazon.ca/Electronic-Bluetooth-Lithium-Battery-Interface/dp/B07YMXZ925) | ESP32 (https://www.aliexpress.com/item/32864722159.html)
 | 48.3 | Nema 17 stepper |  | ali (https://www.aliexpress.com/item/Free-shipping-Nema17-Stepper-Motor-1-5A-Nema-17-step-motor-42BYGH-17HS4401-motor-4-lead/32376023464.html) |  |  | one piece only for Rocker only (https://www.aliexpress.com/item/4000130492082.html?s=p&ad_pvid=202004270834575029870816044440003712899_1)
 | 4 | OLED Display | 1 | ali (https://www.aliexpress.com/item/0-96-inch-IIC-Serial-Yellow-Blue-OLED-Display-Module-128X64-I2C-SSD1306-12864-LCD-Screen/32902463963.html) | amazon ca (https://www.amazon.ca/Kuman-Yellow-Display-Arduino-Raspberry/dp/B01N78FUH7)
 | 8.8 | Heater Pad | 2 | ali (https://www.aliexpress.com/item/Mayitr-12V-DC-20W-Flexible-Waterproof-Silicon-Heater-Pad-Silicone-Heated-Electric-Heating-Pads-80x100mm/32990004646.html) | amazon ca (https://www.amazon.ca/Peristaltic-Aquarium-Laboratory-Chemical-Automatic/dp/B07XXYJRFQ)
 | 36 | Dosing pump 2x4 IDxOD diameter, 12 V, 71 ml/min Used for PH dosage Used for OD and sampling Used for adding media Used for bottom drainage (Optional) | 3 | ali (https://www.aliexpress.com/item/4000398227103.html) | amazonCa 1 month delivery (https://www.amazon.ca/Yanmis-Peristaltic-Laboratory-Bioengineering-32x23mm/dp/B07XTHXM8R)
 | $22.85 | PH sensor | 1 | ali (https://www.aliexpress.com/item/33014998723.html)
http://ee-classes.usc.edu/ee459/library/datasheets/DS18B20.pdf http://ee-classes.usc.edu/ee459/library/datasheets/DS18B20.pdfttps://www.adafruit.com/product/642 | $3.00 | DS18B20 Stainless steel package 1 meter digital temperature sensorhttps://www.aliexpress.com/item/32467815969.html | 1 | aliexpress (https://www.aliexpress.com/item/4000068914916.html)
NOTE: see sensor options and reasoning in the additional document on google drive bioreactor folder | $3.75 | Temp Sensor Sleeve | 1 | ali (https://www.aliexpress.com/item/4000191329563.html?scm_id=1007.14976.158757.0&scm-url=1007.14976.158757.0&_t=g)
 | $2.00 | Silicone nut for temp sleeve | 1 | ali (https://www.aliexpress.com/item/4000027435343.html?spm=a2g0o.cart.0.0.983a3c00MpKbJ6&mp=1)
 | $15.00 | OD sensor | 1 | ali (https://www.aliexpress.com/item/32341715918.html?spm=a2g0s.9042311.0.0.27424c4dsbCzgJ)
 | 9.8 | Wire silicone | 1 | ali (https://www.aliexpress.com/item/1881527180.html?spm=a2g0s.9042311.0.0.27424c4dNvemb9)
 | 9.9 | 5v regulator | 1 | ali (https://www.aliexpress.com/item/LM2596-LED-Driver-DC-DC-Step-down-Adjustable-CC-CV-Power-Supply-Module-Battery-Charger-Adjustable/32580214850.html)
 | 4 | on off switch | 1 | ali (https://www.aliexpress.com/item/6A-120VAC-mini-2-Position-ON-ON-MTS-102-MTS-202-Toggle-Switch-3-Position-MTS/33050504547.html)
 | 2.1 | USB cable | 1 | ali (https://www.aliexpress.com/item/USLION-2m-3m-Micro-USB-Cable-3A-Fast-Charging-Data-Cable-for-Xiaomi-Redmi-4X-Samsung/4000292398339.html)
 | 2.2 | Power jack | 1 | ali (https://www.aliexpress.com/item/10pcs-DC-Power-Jack-Plugs-Male-Female-Socket-Adapter-Connectors-2-1mm-x-5-5mm-For/32949784101.html)
 | 2.5 | Power Jack Socket | 1 | ali (https://www.aliexpress.com/item/10-PCS-LOT-DC022B-3A-12v-DC-Power-Supply-Jack-Socket-Female-Panel-Mount-Connector-5/32825869674.html)
 | $5.2 | MOSFET driver |  | ali (https://www.aliexpress.com/item/5PCS-MOSFET-Button-IRF520-MOSFET-Driver-Module-for-Arduino-For-Raspberry-pi-For-ARM-For-MCU/32858792855.html)
 | $9 | Regular Motor driver DRV8833 /TB6612FNG | 3 | ali (https://www.aliexpress.com/item/4000758777384.html?spm=a2g0o.cart.0.0.11873c00XOPVkz&mp=1)
 |  | Stepper driver DRV8825
 |  | liquid silicone |  | Alumilite (https://www.amazon.ca/Alumilite-Corp-Amazing-Putty-0-66-Pound/dp/B0058VAG5A)
 | $5.72 | silicone bags | 3 | silicone bags (https://www.aliexpress.com/item/4000284324410.html?spm=a2g0s.9042311.0.0.308c4c4db4GAXj) | ebay broken bag (https://www.ebay.co.uk/itm/303513212751?ViewItem=&item=303513212751) | Amazon fast ship 2 liter 25$ (https://www.amazon.ca/gp/product/B075TM3GVX/ref=ppx_yo_dt_b_asin_title_o02_s00?ie=UTF8&psc=1)
 | 15.4 | hose silicone 6mm OD and 4mm ID | 2x5m | ali (https://www.aliexpress.com/item/4000159962222.html?spm=a2g0o.cart.0.0.40663c00pN0GcB&mp=1)
 | 8 | hose fittings silicone fit 4mm ID of hose | 1 | ali (https://www.aliexpress.com/item/32982214864.html?spm=a2g0o.cart.0.0.1c903c00ySrlZY&mp=1) | Ordered from ebay (https://www.ebay.ca/itm/50-pk-DC-048-M8-048P-Plastic-Connector-Barb-Equal-Straight-Male-M8-for-Tube-Hose/163420478292?ssPageName=STRK%3AMEBIDX%3AIT)
 | 8 | hose fittings silicone fit 4mm ID of hose ELBOW | 1 | ali (https://shoppingcart.aliexpress.com/order/confirm_order.htm?objectId=32985071550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)
 | 11 | 2mm silicone sheet for gaskets etc.200 by 200 mm | 1 | ali (https://www.aliexpress.com/item/4000210894016.html)
 | 8.9 | gaskets all sizes | 1 | ali (https://www.aliexpress.com/item/10pcs-1-4-3-8-1-2-3-4-1-20-25-32-40-50mm-Silicon/4000027435343.html)
 | 7.5 | clamps | 1 | ali (https://www.aliexpress.com/item/Siphon-tube-clamp-Home-brew-Silicone-Tube-Clip-Flow-Control-Pipe-Valve-Wine-Beer-Making-Clamp/32969397092.html)
 | 17.4 | dessicant 500g | 1 | ali (https://www.aliexpress.com/item/500g-Waterproof-packaging-bule-orange-Reusable-Silica-Gel-Beads-Moisture-Absorber-Desiccant-Moisture-Absorber-Dehumidifier/330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)
 | 42.6 | 25mm 0.22um Hydrophilic millipore Sterile PTFE Syringe Filter (https://www.aliexpress.com/item/50-Pieces-lots-Lab-25mm-0-22um-Hydrophilic-millipore-Sterile-PTFE-Syringe-Filter/32999216814.html) |  | ali (https://www.aliexpress.com/snapshot/0.html?orderId=8012521694038507&productId=32999216814)
 | 5 | ball bearings |  | ali 10 pieces (https://www.aliexpress.com/item/33051895647.html?spm=a2g0s.9042311.0.0.27424c4d9liA6M) | https://www.aliexpress.com/item/33019684033.html?spm=a2g0s.9042311.0.0.27424c4d9liA6M
 | 2.1 | bearings lubrication oil |  | ali (https://www.aliexpress.com/item/Hot-Sale-1-Bottle-Low-Viscosity-Lubricant-Bearing-Lubricating-Oil-For-Roller-Skate-Drift-Board-Skateboard/4000469090212.html)
 | 27 | air pump |  | ali (https://www.aliexpress.com/item/Super-aquarium-air-pump-cheap-pump-air-compressor-for-aquarium-increase-air-control-aquarium-fish-2/32880892158.html) | 12 volts (https://www.aliexpress.com/item/4000175515842.html) | https://www.aliexpress.com/item/4000175515842.html
Total C$ | 354.02 |  |  |  |  | https://www.aliexpress.com/item/32880892158.html?spm=a2g0s.9042311.0.0.13754c4dUH3CY6
Total Euro | 230.113 |  |  |  |  | https://www.servoflo.com/micropumps
 |  | Optional |  |  |  | https://www.aliexpress.com/item/32827920972.html
 |  |  |  |  |  | https://www.aliexpress.com/wholesale?catId=0&initiative_id=SB_20200503125933&SearchText=diaphram+air+pump
 | 85 used to be 18 in Jan | UV lamp |  | ali (https://www.aliexpress.com/item/E27-30W-UV-quartz-bactericidal-lamp-disinfection-ozone-sterilizer-light-home-kill-mite-sterilization-ultraviolet-tube/32969771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)
 | ALL BOARD ELECTRONIC COMPONENTS are in The board BOM!!!
 |  | pH calibration buffer |  | amazon (https://www.amazon.com/Hanna-Instruments-70007P-Buffer-Solution/dp/B002NX0W0U)
 |  | piezoelectric sonicator |  | ali (https://www.aliexpress.com/item/33010047972.html?spm=a2g0o.cart.0.0.6fc73c00bpiRoG&mp=1)

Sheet: Wet components
name | comment | provider one item | Provider 1
hole puncher | used to punch holes for tubing connectors | get the 8 or 10 pieces | https://www.aliexpress.com/item/1005002381783862.html
heating pad | the heater | 10x10 either 24V or 12 v | https://www.aliexpress.com/item/1005001775429452.html
silicone tubing | Get 10 meters | hose silicone 6mm OD and 4mm ID | https://www.aliexpress.com/item/4000159962222.html?spm=a2g0o.cart.0.0.40663c00pN0GcB&mp=1
tube clamp | Get 4 pieces in total |  | https://www.aliexpress.com/item/32969397092.html?spm=a2g0o.order_list.0.0.21ef1802QmCDfJ
tube connectors with nuts | Get 20 pieces with nuts | Color: 4-M6-4 | https://www.aliexpress.com/item/32982214864.html?spm=a2g0o.order_list.0.0.21ef1802QmCDfJ
tube plain connectors | Get 5 pieces in total | 3.9mm | https://www.aliexpress.com/item/32985936382.html?spm=a2g0o.order_detail.0.0.4805f19ce6FWrx
cuvette |  |  | https://www.aliexpress.com/item/32793994127.html?spm=a2g0o.order_list.0.0.21ef1802eHYD99
silicone bag | Get maybe 2 white or blue 500 ml and one smaller or bigger | 500 ml and 1000 ml | https://www.aliexpress.com/item/4000270320648.html
aeration stone | you might be fine with either .5 micron or 2 micron | 2 micron | https://www.aliexpress.com/item/32986483347.html?spm=a2g0o.order_list.0.0.21ef1802eHYD99

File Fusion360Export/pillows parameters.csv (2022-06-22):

platformTopSmallBallJointHoleDim | mm | 13.2 mm
ballBearingWrapperTubeThickness | mm | 2 mm
stockThickness | mm | 9.6 mm
baseHeight | mm | 7.5 mm
screwsCenterDistance | mm | 22 mm
baseLength | mm | screwsCenterDistance + screwHeadDiam + 3 mm
smallBallJointCenterFromGround | mm | 13.15 mm
screwHoleDiam | mm | 3.5 mm
screwHeadDiam | mm | 6 mm
screwHeadHeight | mm | 2 mm
smallBallJointHeight | mm | 4 mm
linkStockHeight | mm | 12.8 mm
linkWidth | mm | 9.4 mm
linkHoleCenterDistance | mm | 41 mm
linkBallJoinInsertDiam | mm | 8.1 mm
linkBallInsertHeight | mm | 6.8 mm
linkClearanceHeigt | mm | 1 mm
toolDiameter | mm | 2 mm
boxRodDiam | mm | 6.3 mm
boxRodCenterFromGround | mm | 14.5 mm
boxBaseHeight | mm | 18.7 mm
bigBallJointCenterFromGround | mm | 13 mm
bigBallJointHeight | mm | 7 mm
platformTopBigBallJointHoleDim | mm | 22 mm - 1 mm
d142 | mm | stockThickness
d143 | deg | 0.0 °
d12 | mm | baseLength
d13 | mm | baseHeight
d14 | mm | platformTopSmallBallJointHoleDim
d16 | mm | bigBallJointCenterFromGround
d17 | mm | platformTopSmallBallJointHoleDim - 4 mm
d159 | mm | platformTopSmallBallJointHoleDim + 6 mm
d18 | mm | smallBallJointHeight + 0.2 mm
d19 | deg | 0.0 °
d93 | mm | stockThickness - smallBallJointHeight - 0.2 mm
d20 | mm | stockThickness
d21 | deg | 0.0 °
d22 | mm | screwHoleDiam
d29 | mm | stockThickness / 2
d109 | mm | screwsCenterDistance
d110 | mm | screwHeadDiam
d111 | mm | baseLength / 2
d27 | mm | -baseHeight
d28 | deg | 0.0 °
d31 | mm | -baseHeight
d32 | deg | 0.0 °
d33 | mm | -baseHeight
d34 | deg | 0.0 °
d35 | mm | -screwHeadHeight
d36 | deg | 0.0 °
d37 | mm | -screwHeadHeight
d38 | deg | 0.0 °
d39 | mm | -baseHeight
d40 | deg | 0.0 °
d101 | mm | stockThickness
d102 | deg | 0.0 °
d154 |  | 1
d155 | mm | 0.6 mm
d45 | mm | stockThickness + 0.3 mm
d46 | mm | 1.2 mm
d47 | mm | 2.2 mm
d49 | mm | ( baseLength - screwsCenterDistance ) / 2
d59 | mm | stockThickness
d60 | mm | ( stockThickness + 0.2 mm ) / 2
d51 | mm | 3 mm
d52 | deg | 0.0 °
d53 | mm | 6 mm
d54 | deg | 0.0 °
d55 | mm | stockThickness
d56 | deg | 0 °
d67 | mm | linkHoleCenterDistance + linkBallJoinInsertDiam + 2 mm
d68 | mm | linkWidth
d69 | mm | linkBallJoinInsertDiam
d70 | mm | linkWidth / 2
d71 | mm | linkHoleCenterDistance
d72 | mm | 2.01 mm
d94 | mm | 10 mm
d73 | mm | linkStockHeight - linkBallInsertHeight
d74 | deg | 0.0 °
d75 | mm | linkStockHeight
d76 | deg | 0.0 °
d77 |  | 1
d78 | mm | 1 mm
d97 |  | 1
d98 | mm | 1 mm
d99 |  | 1
d100 | mm | 1 mm
d95 | mm | linkStockHeight - linkBallInsertHeight + 0.8 mm
d96 | deg | 0.0 °
d119 | mm | baseLength
d124 | mm | boxRodDiam
d128 | mm | boxRodCenterFromGround
d129 | mm | baseHeight
d141 | mm | 3 mm
d150 | mm | 7 mm
d151 | mm | 8.741394 mm
d130 | mm | stockThickness
d131 | deg | 0.0 °
d132 | mm | baseLength / 2
d133 | mm | stockThickness / 2
d134 | mm | screwHoleDiam
d135 | mm | screwHeadDiam
d136 | mm | screwsCenterDistance
d137 | mm | -baseHeight
d138 | deg | 0.0 °
d139 | mm | -screwHeadHeight
d140 | deg | 0.0 °
d144 | mm | stockThickness
d145 | deg | 0.0 °
d148 |  | 1
d149 | mm | 0.6 mm
d152 |  | 1
d153 | mm | 4 mm

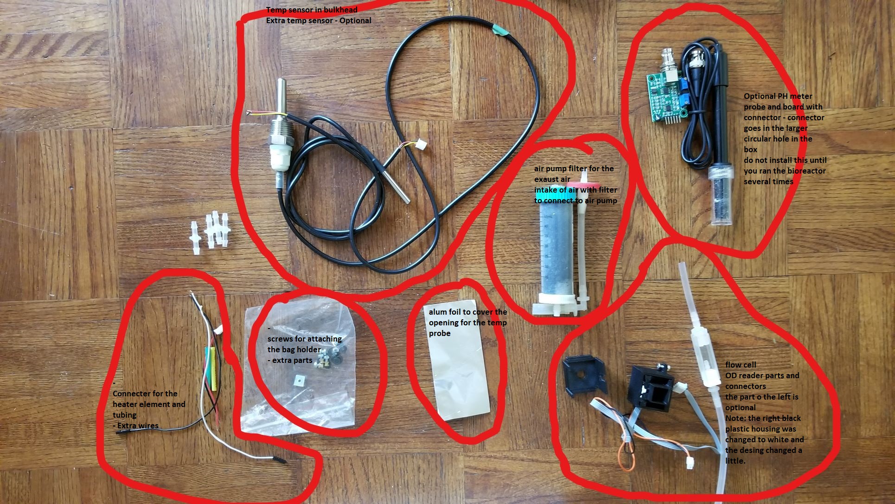
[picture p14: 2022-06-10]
docs/images/parts.jpg

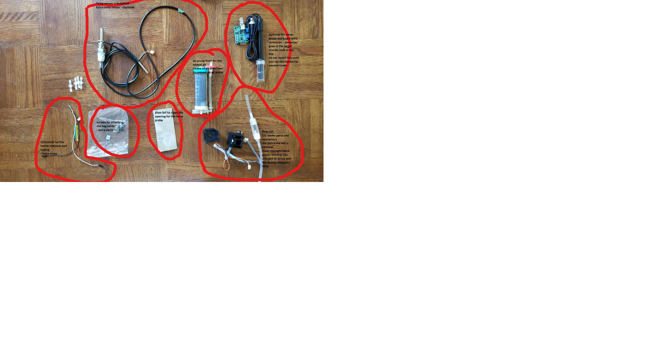
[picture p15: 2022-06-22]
docs/images/real bioreactor parts.png

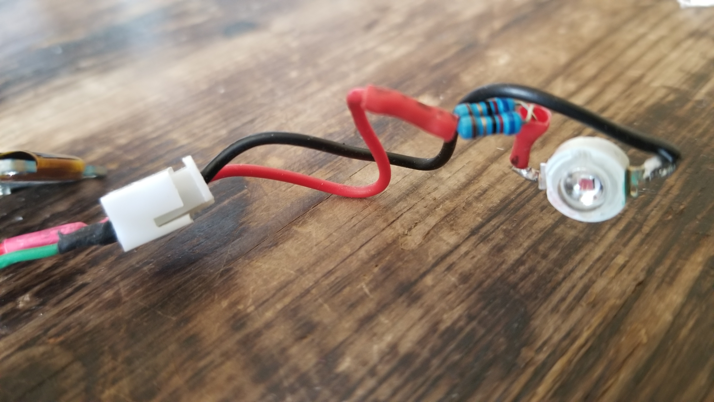
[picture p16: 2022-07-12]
OdMeter/standalone parts/LED and 2 resistors in parallel for power dissipation.jpg

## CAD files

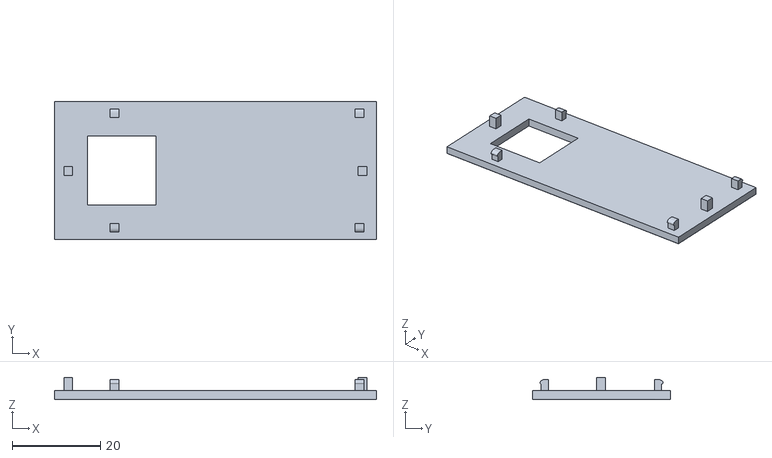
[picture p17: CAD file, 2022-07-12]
Fusion360Export/OD lid jenny.stl
72.8 x 31.2 x 5.00

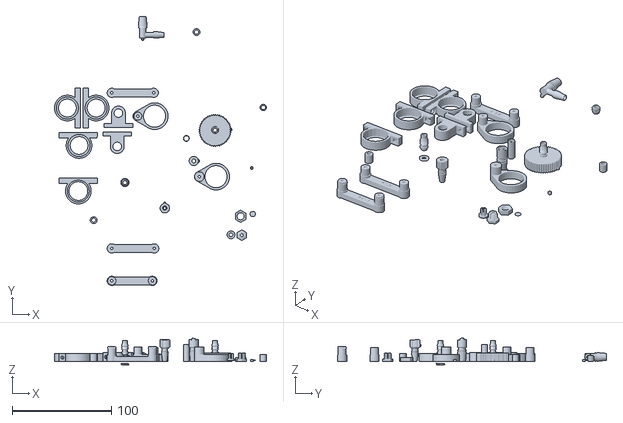
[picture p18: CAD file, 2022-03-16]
mechanical/bioreactor/parts/rocker parts 19 (4).stl
213.9 x 271.4 x 26.8

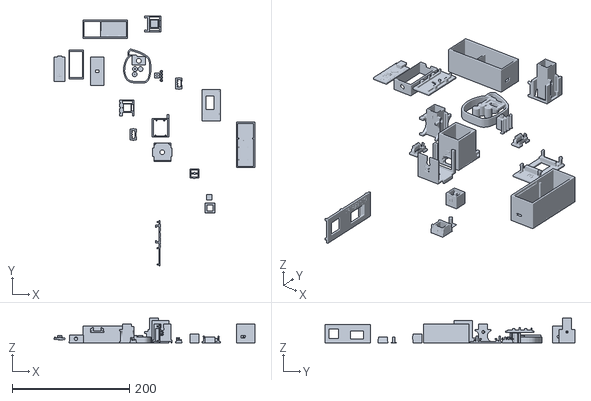
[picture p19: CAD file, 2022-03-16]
otherProjects/opticalDensity/OD reader 16 (13).stl
341.5 x 425.6 x 42.0

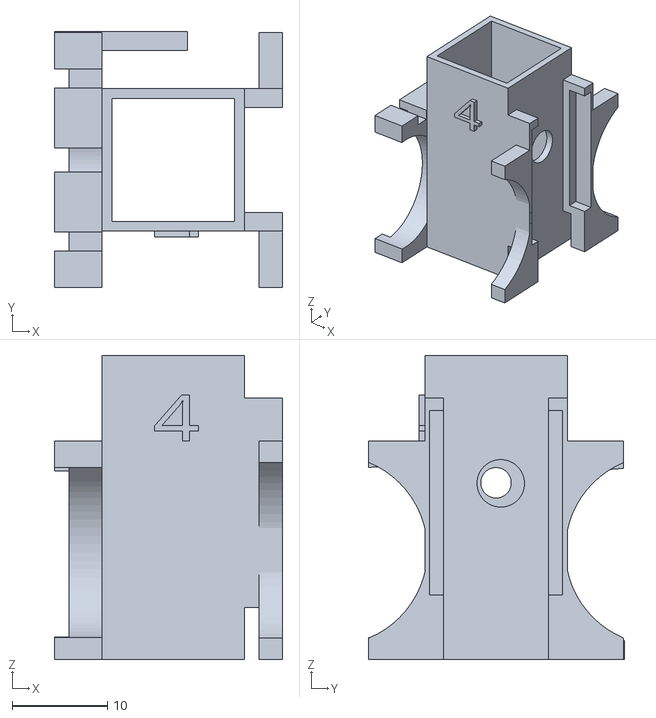
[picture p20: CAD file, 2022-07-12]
Fusion360Export/OD interior Jenny.stl
24.0 x 26.9 x 32.0

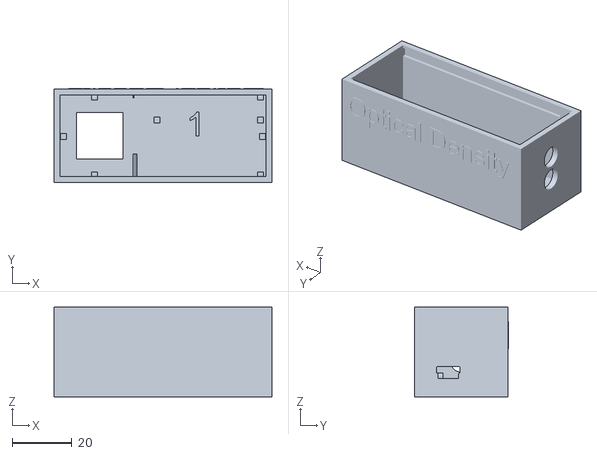
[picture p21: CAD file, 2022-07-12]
Fusion360Export/OD case jenny.stl
72.8 x 31.5 x 30.0

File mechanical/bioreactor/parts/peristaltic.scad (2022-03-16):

// Planetary peristaltic pump (customizable)
// by Drmn4ea (drmn4ea at google's mail)
// http://tim.cexx.org/projects/3d/peristaltic.scad
// Released under the Creative Commons - Attribution - Share Alike license (http://creativecommons.org/licenses/by-sa/3.0/)
//
// Adapted from Emmett Lalish's Planetary Gear Bearing at http://www.thingiverse.com/thing:53451


// --------  Printer-related settings ------------

// Clearance to generate between non-connected parts. If the gears print 'stuck together' or are difficult to separate, try increasing this value. If there is excessive play between them, try lowering it. (default: 0.15mm)
tol=0.15;

// Allowed overhang for overhang removal; between 0 and 0.999 (0 = none, 0.5 = 45 degrees, 1 = infinite)
allowed_overhang = 0.75;


// --------  Details of the tubing used in the pump, in mm ------------

// Outer diameter of your tubing in mm
tubing_od = 6;

// Wall thickness of your tubing
tubing_wall_thickness = 1;
// Amount the tubing should be compressed by the rollers, as a proportion of total thickness (0 = no squish, 1.0 = complete squish)
tubing_squish_ratio = 0.5;


// --------  Part geometry settings ------------

// Approximate outer diameter of ring in mm
D=51.7;

// Thickness i.e. height in mm
T=15;

// Number of planet gears
number_of_planets=3;

// Number of teeth on planet gears
number_of_teeth_on_planets=7;

// Number of teeth on sun gear (approximate)
approximate_number_of_teeth_on_sun=9;

// pressure angle
P=45;//[30:60]

// number of teeth to twist across
nTwist=1;

// width of hexagonal hole
w=6.7;

DR=0.5*1;// maximum depth ratio of teeth


// ----------------End of customizable values -----------------

m=round(number_of_planets);
np=round(number_of_teeth_on_planets);
ns1=approximate_number_of_teeth_on_sun;
k1=round(2/m*(ns1+np));
k= k1*m%2!=0 ? k1+1 : k1;
ns=k*m/2-np;
echo(ns);
nr=ns+2*np;
pitchD=0.9*D/(1+min(PI/(2*nr*tan(P)),PI*DR/nr));
pitch=pitchD*PI/nr;
echo(pitch);
helix_angle=atan(2*nTwist*pitch/T);
echo(helix_angle);

phi=$t*360/m;

// compute some parameters related to the tubing
tubing_squished_width = tubing_od * (PI/2);
tubing_depth_clearance = 2*(tubing_wall_thickness*(1-tubing_squish_ratio));

// temporary variables for computing the outer radius of the outer ring gear teeth
// used to make the clearance for the peristaltic squeezer feature on the planets
outerring_pitch_radius = nr*pitch/(2*PI);
outerring_depth=pitch/(2*tan(P));
outerring_outer_radius = tol<0 ? outerring_pitch_radius+outerring_depth/2-tol : outerring_pitch_radius+outerring_depth/2;

// temporary variables for computing the outer radius of the planet gear teeth
// used to make the peristaltic squeezer feature on the planets
planet_pitch_radius = np*pitch/(2*PI);
planet_depth=pitch/(2*tan(P));
planet_outer_radius = tol<0 ? planet_pitch_radius+planet_depth/2-tol : planet_pitch_radius+planet_depth/2;

// temporary variables for computing the inside & outside radius of the sun gear teeth
// used to make clearance for planet squeezers
sun_pitch_radius = ns*pitch/(2*PI);
sun_base_radius = sun_pitch_radius*cos(P);
echo(sun_base_radius);
sun_depth=pitch/(2*tan(P));
sun_outer_radius = tol<0 ? sun_pitch_radius+sun_depth/2-tol : sun_pitch_radius+sun_depth/2;
sun_root_radius1 = sun_pitch_radius-sun_depth/2-tol/2;
sun_root_radius = (tol<0 && sun_root_radius1<sun_base_radius) ? sun_base_radius : sun_root_radius1;
sun_min_radius = max (sun_base_radius,sun_root_radius);

// debug raw gear shape for generating overhang removal
//translate([0,0,5])
//{
//	//halftooth (pitch_angle=5,base_radius=1, min_radius=0.1,	outer_radius=5,	half_thick_angle=3);
//	gear2D(number_of_teeth=number_of_teeth_on_planets, circular_pitch=pitch, pressure_angle=P, depth_ratio=DR, clearance=tol);
//}

translate([0,0,T/2])
{
	// outer ring
	difference()
	{
		// HACK: Add tubing depth clearance value to the total OD, otherwise the outer part may be too thin. FIXME: This is a quick n dirty way and makes the actual OD not match what the user entered...
		cylinder(r=D/2 + tubing_depth_clearance,h=T,center=true,$fn=100);
		exitholes(outerring_outer_radius-tubing_od/4,tubing_od, len=100);
		union()
		{
			// HACK: On my printer, it seems to need extra clearance for the outside gear, trying double...
			herringbone(nr,pitch,P,DR,-2*tol,helix_angle,T+0.2);
			cylinder(r=outerring_outer_radius+tubing_depth_clearance,h=tubing_squished_width,center=true,$fn=100);
			// overhang removal for top teeth of outer ring: create a frustum starting at the top surface of the "roller" cylinder 
			// (which will actually be cut out of the outer ring) and shrinking inward at the allowed overhang angle until it reaches the
			// gear root diameter.
			translate([0, 0, tubing_squished_width/2])
			{
				cylinder(r1=outerring_outer_radius+tubing_depth_clearance, r2=outerring_depth,h=abs(outerring_outer_radius+tubing_depth_clearance - outerring_depth)/tan(allowed_overhang*90),center=false,$fn=100);
			}
		}
	}



	// sun gear
	rotate([0,0,(np+1)*180/ns+phi*(ns+np)*2/ns])
	
	difference()
	{

		// the gear with band cut out of the middle
		difference()
		{
			mirror([0,1,0])
				herringbone(ns,pitch,P,DR,tol,helix_angle,T);
				// center hole
				cylinder(r=w/sqrt(3),h=T+1,center=true,$fn=6);
				// gap for planet squeezer surface
				difference()
				{
					cylinder(r=sun_outer_radius,h=tubing_squished_width,center=true,$fn=100);
					cylinder(r=sun_min_radius-tol,h=tubing_squished_width,center=true,$fn=100);
				}
		}

		// on the top part, cut an angle on the underside of the gear teeth to keep the overhang to a feasible amount
		translate([0, 0, tubing_squished_width/2])
		{
			difference()
			{
				// in height, numeric constant sets the amount of allowed overhang after trim.
				//h=abs((sun_min_radius-tol)-sun_outer_radius)*(1-allowed_overhang)
				// h=tan(allowed_overhang*90)
				cylinder(r=sun_outer_radius,h=abs((sun_min_radius-tol)-sun_outer_radius)/tan(allowed_overhang*90),center=false,$fn=100);
				cylinder(r1=sun_min_radius-tol, r2=sun_outer_radius,h=abs((sun_min_radius-tol)-sun_outer_radius)/tan(allowed_overhang*90),center=false,$fn=100);
			}
		}
	
	}



	// planet gears

	for(i=[1:m])
	{

		rotate([0,0,i*360/m+phi])
		{
		
			translate([pitchD/2*(ns+np)/nr,0,0])
			{
				rotate([0,0,i*ns/m*360/np-phi*(ns+np)/np-phi])
				{
					union()
					{
						herringbone(np,pitch,P,DR,tol,helix_angle,T);
						// Add a roller cylinder in the center of the planet gears.
						// But also constrain overhangs to a sane level, so this is kind of a mess...
						intersection()
						{
							// the cylinder itself
							cylinder(r=planet_outer_radius,h=tubing_squished_width-tol,center=true,$fn=100);

							// Now deal with overhang on the underside of the planets' roller cylinders.
							// create the outline of a gear where the herringbone meets the cylinder;
							// make its angle match the twist at this point.
							// Then difference this flat gear from a slightly larger cylinder, extrude it with an
							// outward-growing angle, and cut the result from the cylinder.
							planet_overhangfix(np, pitch, P, DR, tol, helix_angle, T, tubing_squished_width, allowed_overhang);

						}

					}

				}
			}
		}
	}
	
}


module planet_overhangfix(
	number_of_teeth=15,
	circular_pitch=10,
	pressure_angle=28,
	depth_ratio=1,
	clearance=0,
	helix_angle=0,
	gear_thickness=5,
	tubing_squished_width,
	allowed_overhang)
{

	height_from_bottom =  (gear_thickness/2) - (tubing_squished_width/2);
	pitch_radius = number_of_teeth*circular_pitch/(2*PI);
	twist=tan(helix_angle)*height_from_bottom/pitch_radius*180/PI; // the total rotation angle at that point - should match that of the gear itself



	translate([0,0, -tubing_squished_width/2]) // relative to center height, where this is used
	{
		// FIXME: This calculation is most likely wrong...
		//rotate([0, 0, helix_angle * ((tubing_squished_width-(2*tol))/2)])
		rotate([0, 0, twist])
		{
			// want to extrude to a height proportional to the distance between the root of the gear teeth
			// and the outer edge of the cylinder
			linear_extrude(height=tubing_squished_width-clearance,twist=0,slices=6, scale=1+(1/(1-allowed_overhang)))
			{
				gear2D(number_of_teeth=number_of_teeth, circular_pitch=circular_pitch, pressure_angle=pressure_angle, depth_ratio=depth_ratio, clearance=clearance);
			}
		}
	}
}

module exitholes(distance_apart, hole_diameter)
{
	translate([distance_apart, len/2, 0])
	{
		rotate([90, 0, 0])
		{
			cylinder(r=hole_diameter/2,h=len,center=true,$fn=100);
		}
	}
	
	mirror([1,0,0])
	{
		translate([distance_apart, len/2, 0])
		{
			rotate([90, 0, 0])
			{
				cylinder(r=hole_diameter/2,h=len,center=true,$fn=100);
			}
		}
	}
}

module rack(
	number_of_teeth=15,
	circular_pitch=10,
	pressure_angle=28,
	helix_angle=0,
	clearance=0,
	gear_thickness=5,
	flat=false){
addendum=circular_pitch/(4*tan(pressure_angle));
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

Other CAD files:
Fusion360Export/Adrian Projects/bioreactor/12 bioreactor 6 mm finger almost manufacture_v8.f3d
Fusion360Export/Adrian Projects/bioreactor/1_v2.f3d
Fusion360Export/Adrian Projects/bioreactor/2 renamed and all sketch stabilized_v1.f3d
Fusion360Export/Adrian Projects/bioreactor/2_v4.f3d
Fusion360Export/Adrian Projects/bioreactor/3 all box and content for OS_v1.f3d
Fusion360Export/Adrian Projects/bioreactor/3_v12.f3d
Fusion360Export/Adrian Projects/bioreactor/4 bioreactor component_v18.f3d
Fusion360Export/Adrian Projects/bioreactor/4 bioreactor_v11.f3d
Fusion360Export/Adrian Projects/bioreactor/5 bioreactor_v5.f3d
Fusion360Export/Adrian Projects/bioreactor/6 bioreactor_v32.f3d
Fusion360Export/Adrian Projects/bioreactor/7 bioreactor_v7.f3d
Fusion360Export/Adrian Projects/bioreactor/8 bioreactor 6 mm finger_v17.f3d
Fusion360Export/Adrian Projects/bioreactor/9 bioreactor 6 mm finger_v2.f3d
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

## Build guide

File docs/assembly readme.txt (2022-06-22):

cut the box and clean using a box cutter
assemble the box
disassemble the box
mount the main pcb
create the ODMeter parts as in the ODMeter readme file
including mounting the constant  current board and the bracket
mount the stepper on the bracket using BOM 3mm diam screws of 12 or 9?? lenght and siione washers
cut 2 under platform pillows
insert 2 small ball bearings in it
cut the central under platform ballbearing pillow
cut 2 over the box pillows
cut link
cut joint ballbearing part
put the platorm over the box and attach the rod
place the motor link aluminum connector between the link and shaft of the motor
tighten the screws gradually to ensure centered and unrestricted motion of the motor

---
other motors
Solder 2 wires about 15 to 25 cm for both the air pump and the circulation peristaltic pump. Use heat shrink. On the other ends, crimp or solder a two pin conectors. You can twist each pair of wire to look neater unless the are already attached lengthwise. Mark with  red marker or black marker where the + and minus will be for the desired spin direction. The motors can be connecected any way but they spin in different directions and both the air and circulation should be kept in the same direction. You can if needed adjust the flow by connecting the silicone tubes in a reverse position.

Cut a foam pad for the air pump and screw the air motor on it with BOM 3mm screws of ??? length connect the motor cables to the main board
Place the peristaltic pump and screw it with BOM 3mm screws of ??? length connect the motor cables to the main board

Software
Create and save a config file for the old board. Use MOS 1 heater MOS 2 Air, A1B1? Bridge for circulation peristaltic pump
connect cable and load software
start coolTerm and configure port and in options /terminal change to Terminal Mode=Line Mode and  EnterKey Emulation=LF
connect and then type ? to see commands
then copy the appropriate config.json from the source code in memory that should begin with: {"name":"standby","standby":false,"targetTemperature":-1000 etc...
then execute 
createFileWithContent /standby.json Paste_here_the _long _string_of_configuration_from_memory
after that load the protocol by executing:
p load standby.json please note that file commands require / while protocol commands like p do not require directory information as we assume all in the root

PP1 -heater works,  PP2 does not work, A1B1 does not work, buzzer works, rocker ? we don't know

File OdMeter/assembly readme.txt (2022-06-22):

The cuvette end has to be cut
Two silicone corks have to be poured

Adjust the current:
	Adjust the voltage pot to maybe -5 volts rom the pot near Input
	Short the output on a 10 AMp scale and adjust the current pot (near output) to about 200 mA until the max light with water cuette about 15-20000

Cut the long cable with 6 wires
Solder the cable to sensor and LED. Solder the other ends to the 2 pin connector and a 4 pin connector for the sensor. 
Wrap the cable around the 3D printed outer case. Add heat shrink parts.
With 2 more wires Solder the const current output to the connector. With 2 extra red black wire solder from constant current input board to another 2 pin connector DONE that will go to the main board VCC. Add heat shrink parts.
So the constant current board needs to be with 2 connectors coming out
mount the costant current using BOM 2x 9 mm 2 mm diam screws

	print the cell flow inner part in black
	print the cell low ODMeter outer housing
	push the sensor and LED inthe slots on the inner part making sure the sensor is aligned with the LED. Sometimes you eed to sand the edges of the sensor board to fit perfectly in the plastic slot. Wipe the actual sensor in case it has fingerprints or or got dirty in the handling
Connect the redBlue LED connector to vcc and Ground on the main board
Connect the I2c connector to I2c on the main board

test with TestOdMeter from VSC. Q is the TestODMeter in GIT?
make sure lank gives at least 13 000 lux measurement value

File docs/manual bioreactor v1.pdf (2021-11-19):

## Configuration and setup management Bioreactor v1

Content

## Device mapping

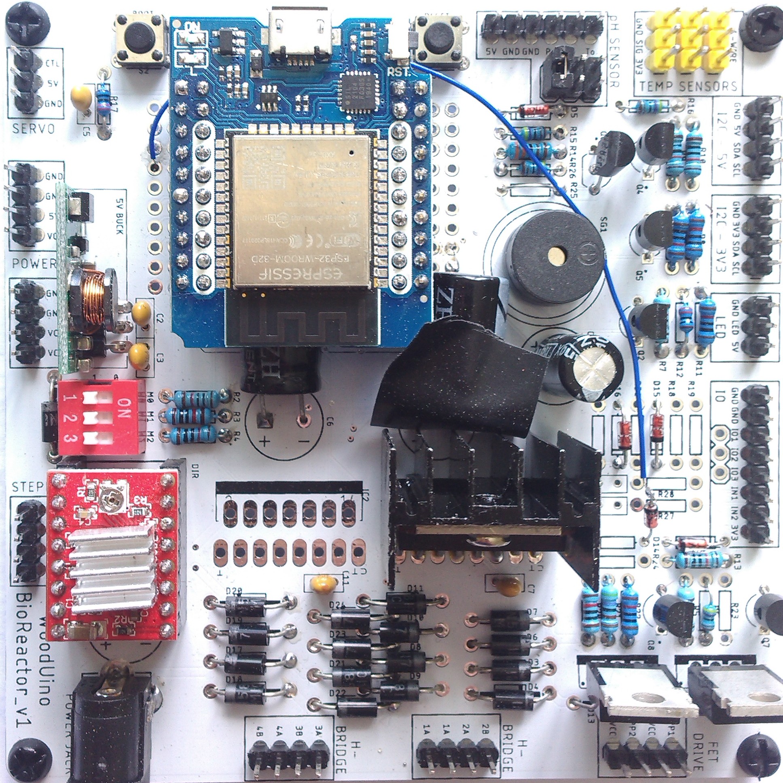
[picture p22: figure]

Pic 1. Board schematic

Currently software supports three sensors – for temperature, PH measurement and light intensity.
1. To hook up temperature, use DS18B20 probe and connect it to any of 3 connection ports (Pic 1 temp sensors pins).
2. PH sensor wiring described below in details, just one thing to remember – it has to be calibrated before using.
3. Light sensor is an I2C device here, can be connected to any of I2C pins on the board. Tested with BH1750 sensor.

There are 8 devices managed by reactor:

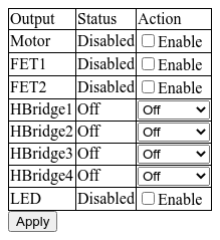
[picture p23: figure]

Pic 2. Main page pane with devices state, every state can be altered

1. Motor – STEPPER pins (refer to Pic 1 here and further). NEMA cable can be connected in forward and reverse way.
2. FET1 - fet drive PP1, VCC pins. Designed to provide permanent power supply.
3. FET2 – fet drive PP2, VCC pins.
4. Hbridge1 – h-bridge 1A, 1A(board misprint ) pins. Designed for intermittent supply.
5. Hbridge2 – h-bridge 2A, 2B pins
6. Hbridge3 – h-bridge 3A, 3B pins
7. Hbridge4 – h-bridge 4A, 4B pins
8. LED – led\GND\5V pins. Can be attached to be on or off by default

## Wi-Fi setup

1. Connect to the device

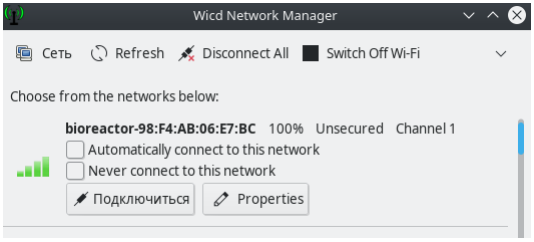
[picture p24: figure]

2. Open in your browser http://bioreactor.local/settings, or http:// 192.168.4.1/settings and
enter your WiFi point name and pass, then save it.

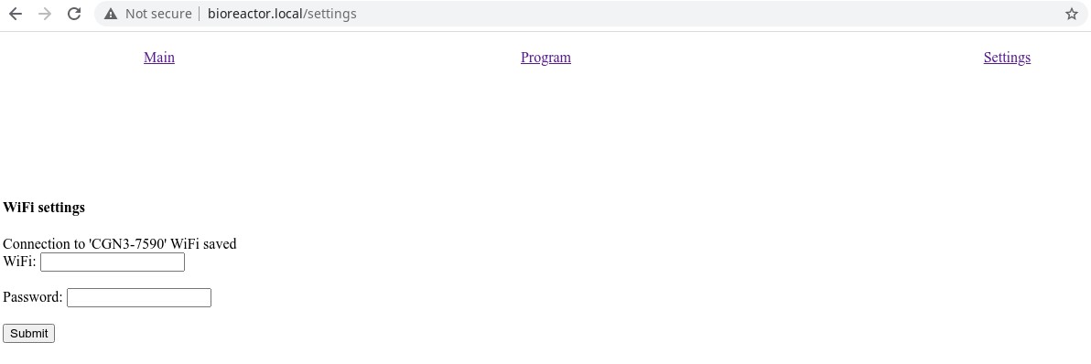
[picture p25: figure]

3. reboot the device. You can then connect to your wifi and access the reactor by visiting http://bioreactor.local/

# PH meter wiring

PH Probe connection is a straightforwad process, one thing to note however is that cable has to be twisted, so that Vcc pin on the reactor board will match Vcc pin on ph board

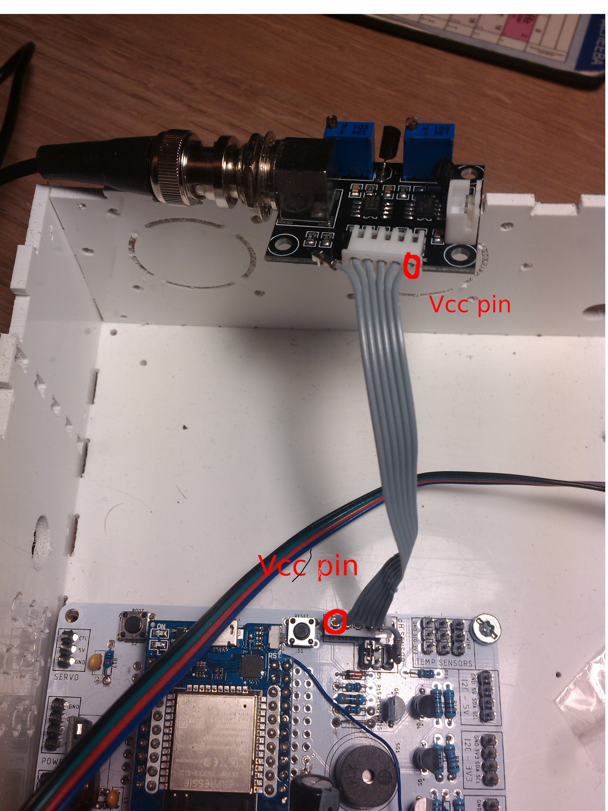
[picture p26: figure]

# Firmware upgrade

1. Open http://bioreactor.local/settings page.
2. Click on ‘Choose file’ button of ‘Update ESP32 firmware’ section and find ’bioreactor.bin’ file on your file system

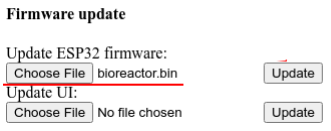
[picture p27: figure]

3. Click update and wait till confirmation appears

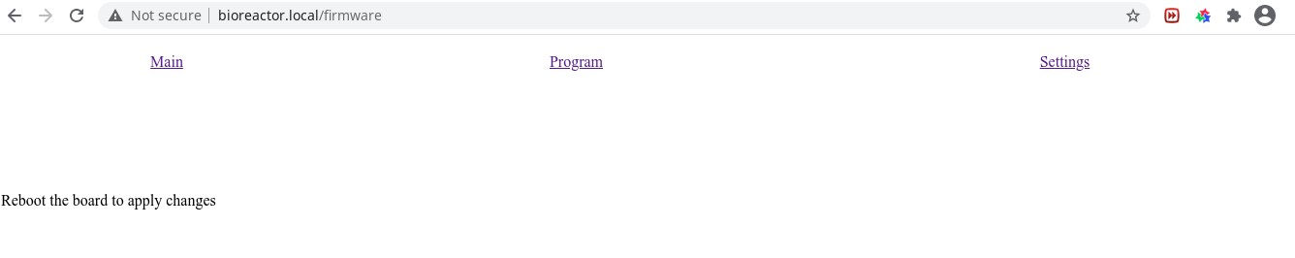
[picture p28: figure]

4. After rebooting your fimrware should be updated

# Updating UI files

1. Open http://bioreactor.local/settings page.
2. Click on ‘Choose file’ button of ‘Update UI’ section and find html or js file on your file system
3. Click update. You should be able to see confirmation promptly. No reboot required, new changes should be applied immediately

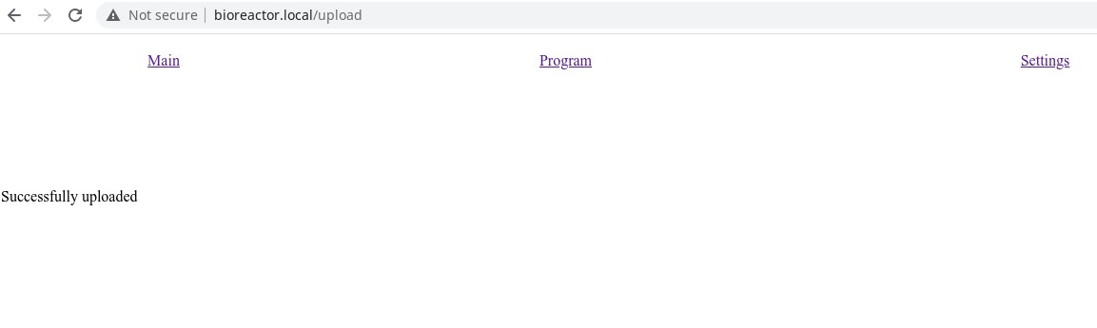
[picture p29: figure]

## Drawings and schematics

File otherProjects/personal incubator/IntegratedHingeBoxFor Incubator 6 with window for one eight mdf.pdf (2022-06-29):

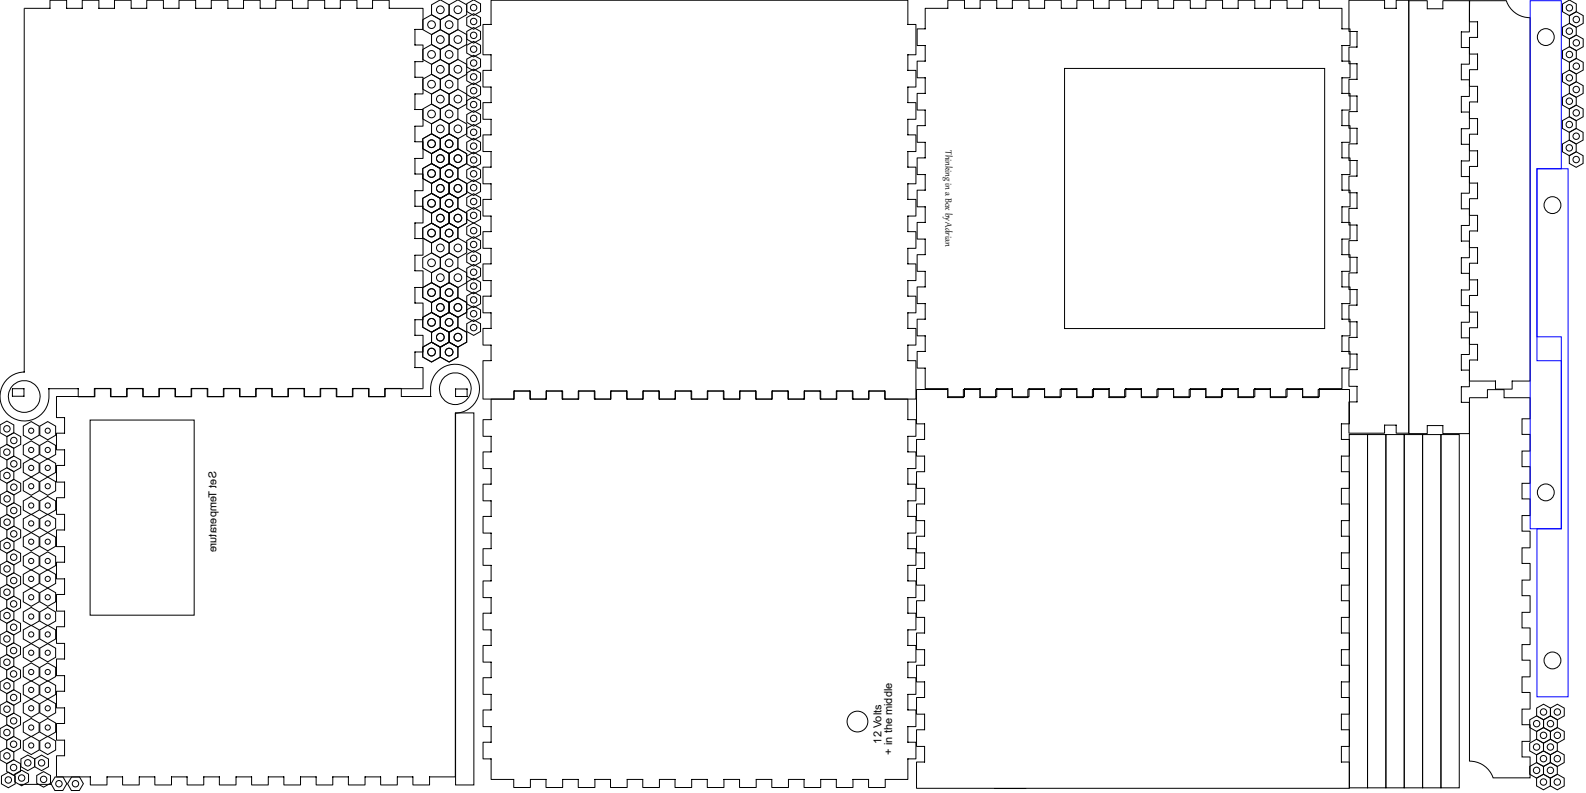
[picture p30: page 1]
12 Volts; Set Temperature

Thinking in a Box by Adrian

+ in the middle

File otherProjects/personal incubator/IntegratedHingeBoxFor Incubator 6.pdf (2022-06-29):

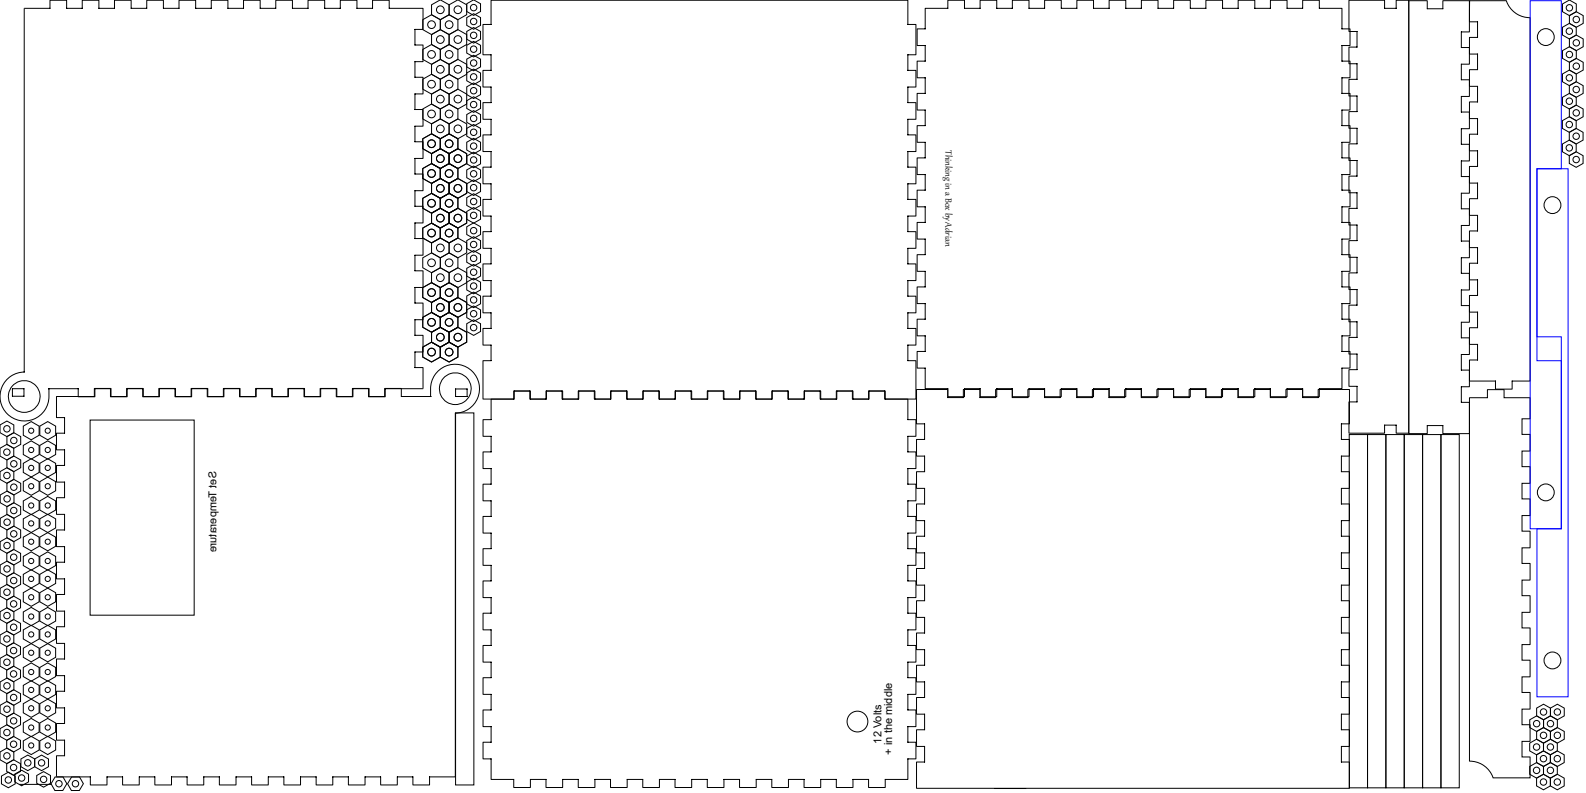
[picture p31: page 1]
12 Volts; Set Temperature

Thinking in a Box by Adrian

+ in the middle

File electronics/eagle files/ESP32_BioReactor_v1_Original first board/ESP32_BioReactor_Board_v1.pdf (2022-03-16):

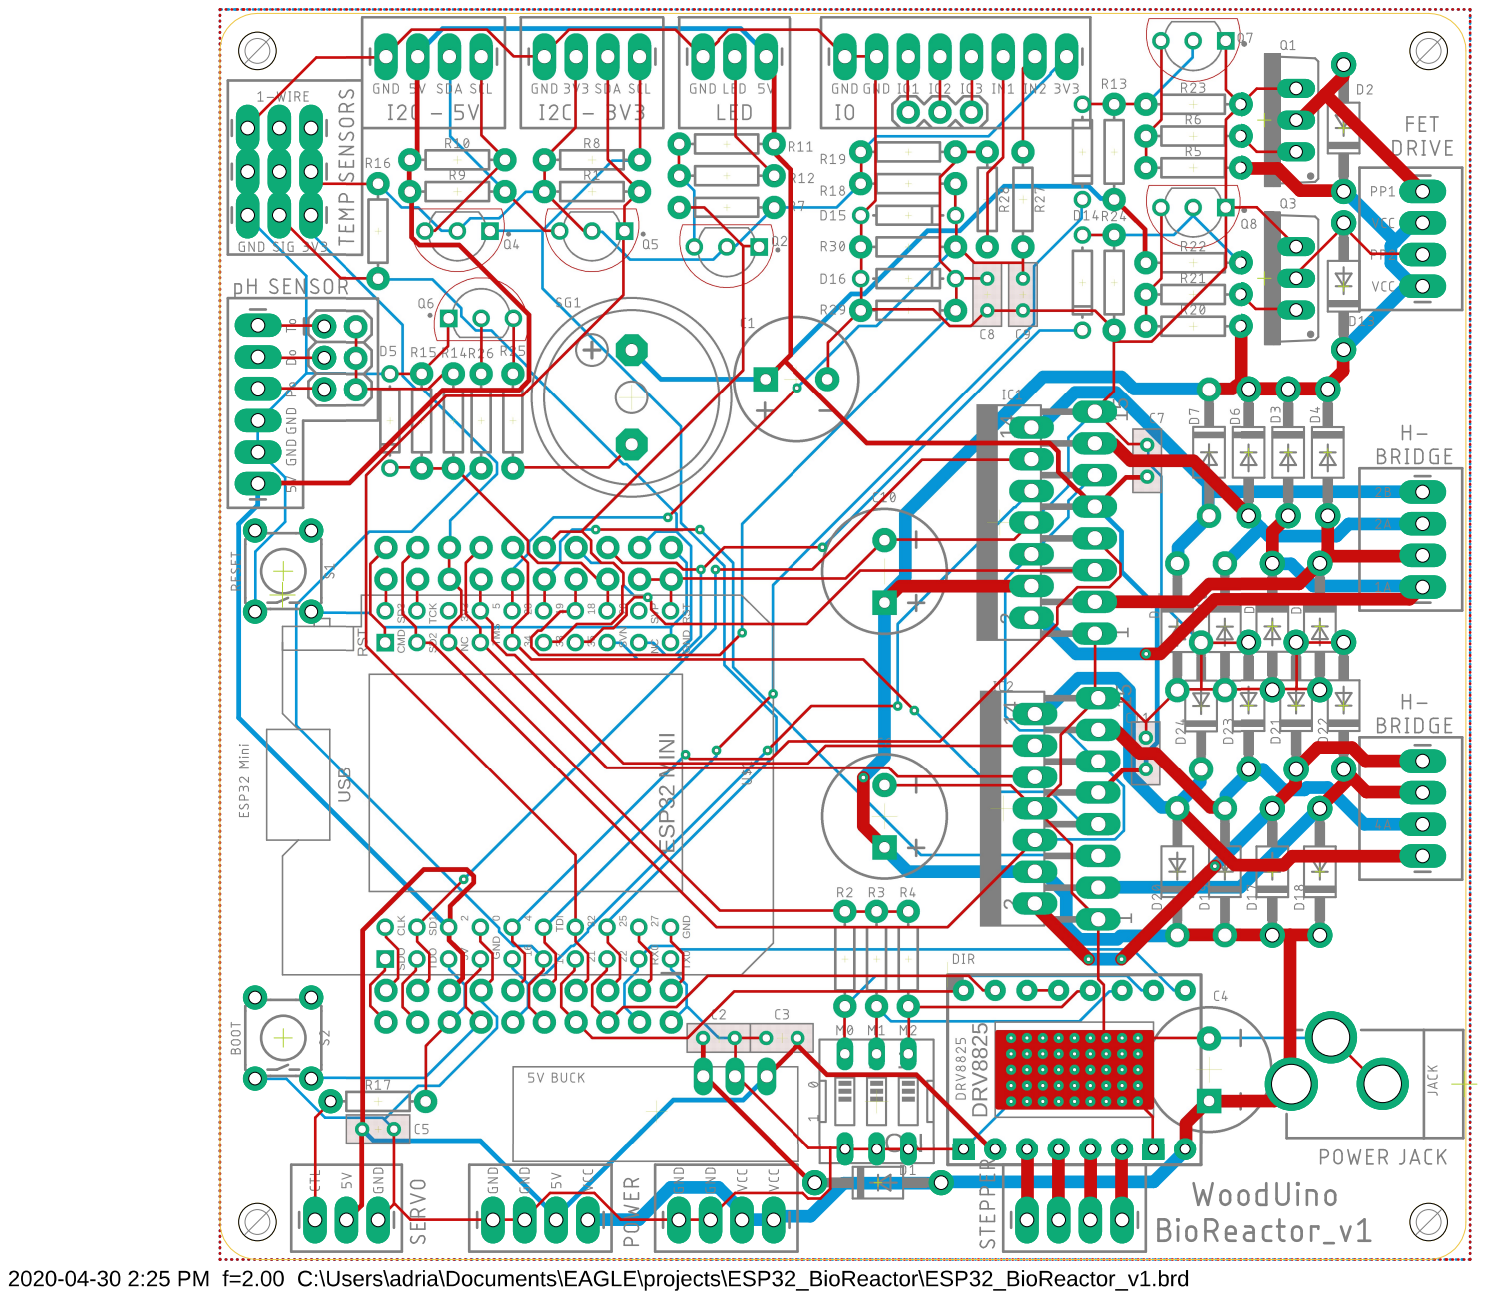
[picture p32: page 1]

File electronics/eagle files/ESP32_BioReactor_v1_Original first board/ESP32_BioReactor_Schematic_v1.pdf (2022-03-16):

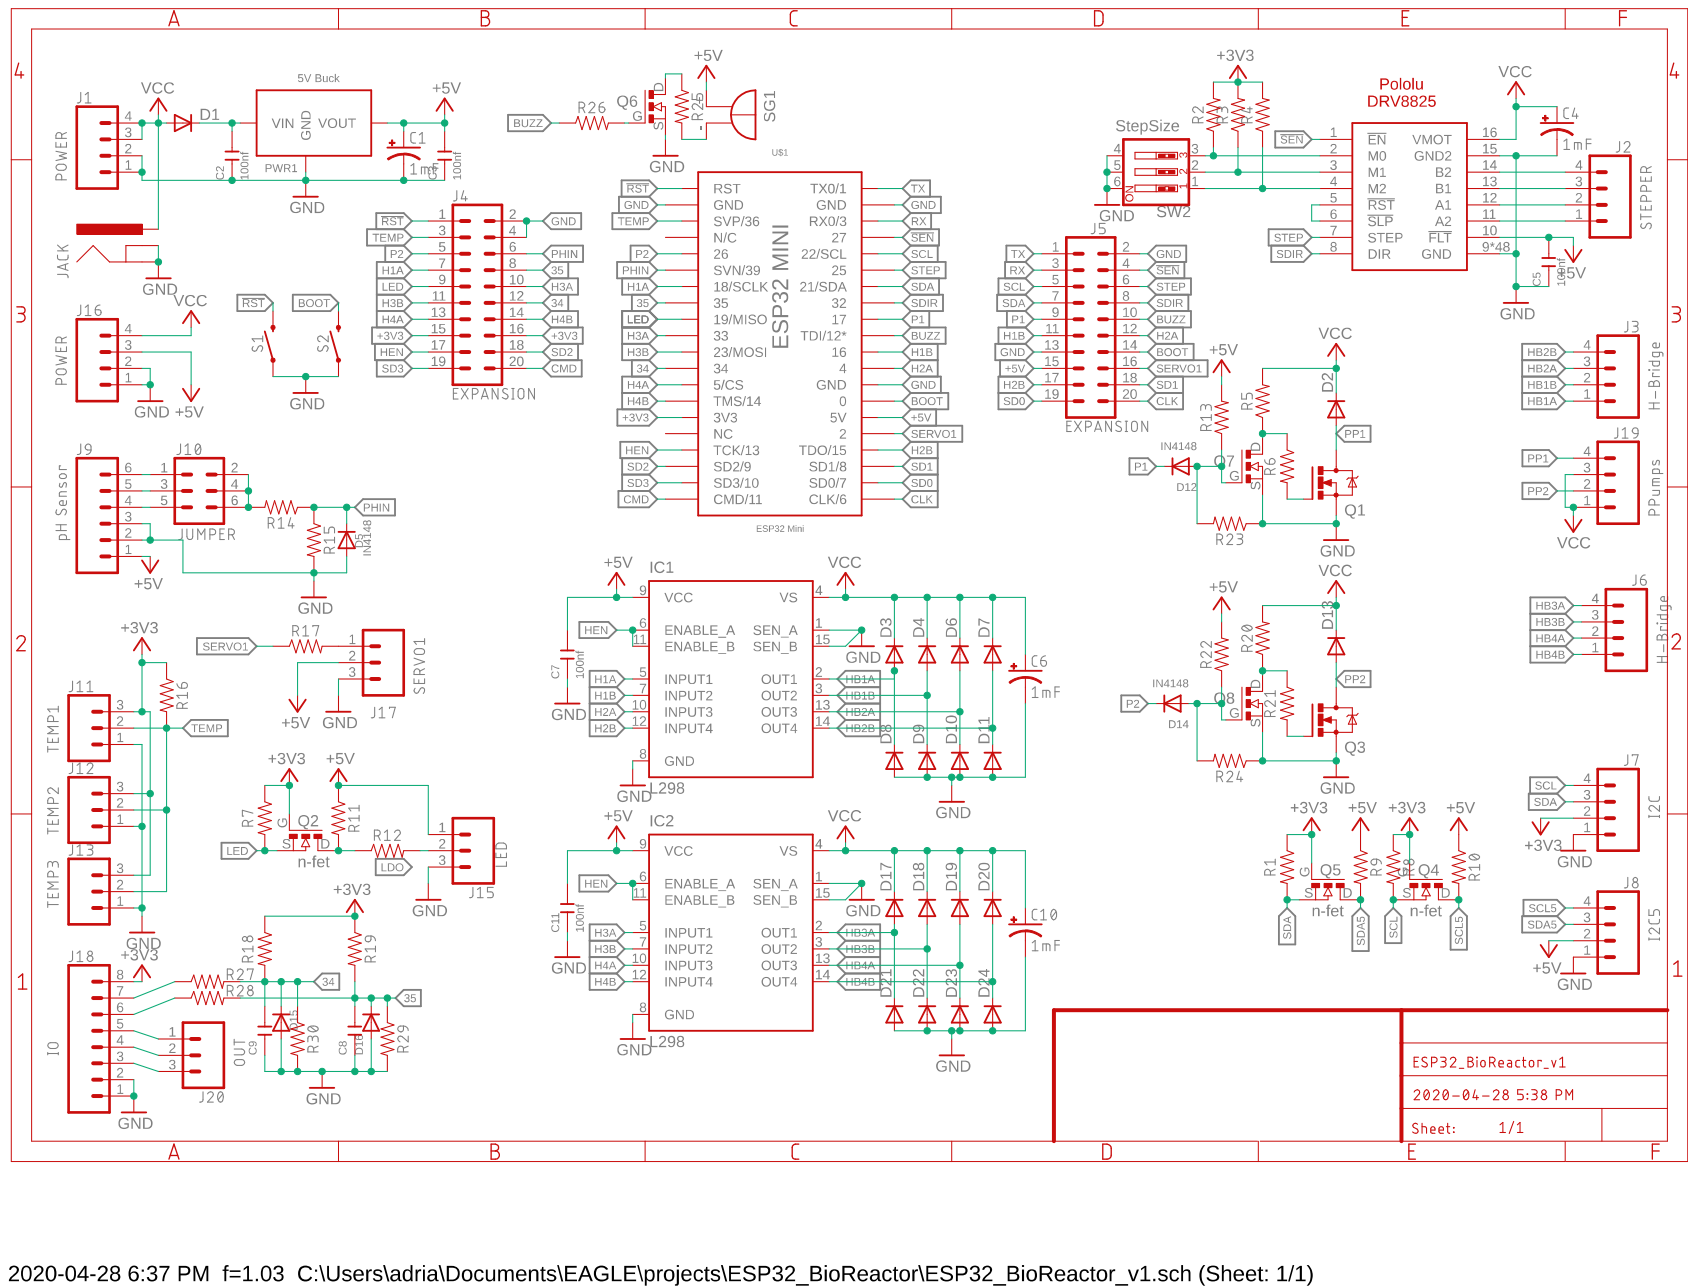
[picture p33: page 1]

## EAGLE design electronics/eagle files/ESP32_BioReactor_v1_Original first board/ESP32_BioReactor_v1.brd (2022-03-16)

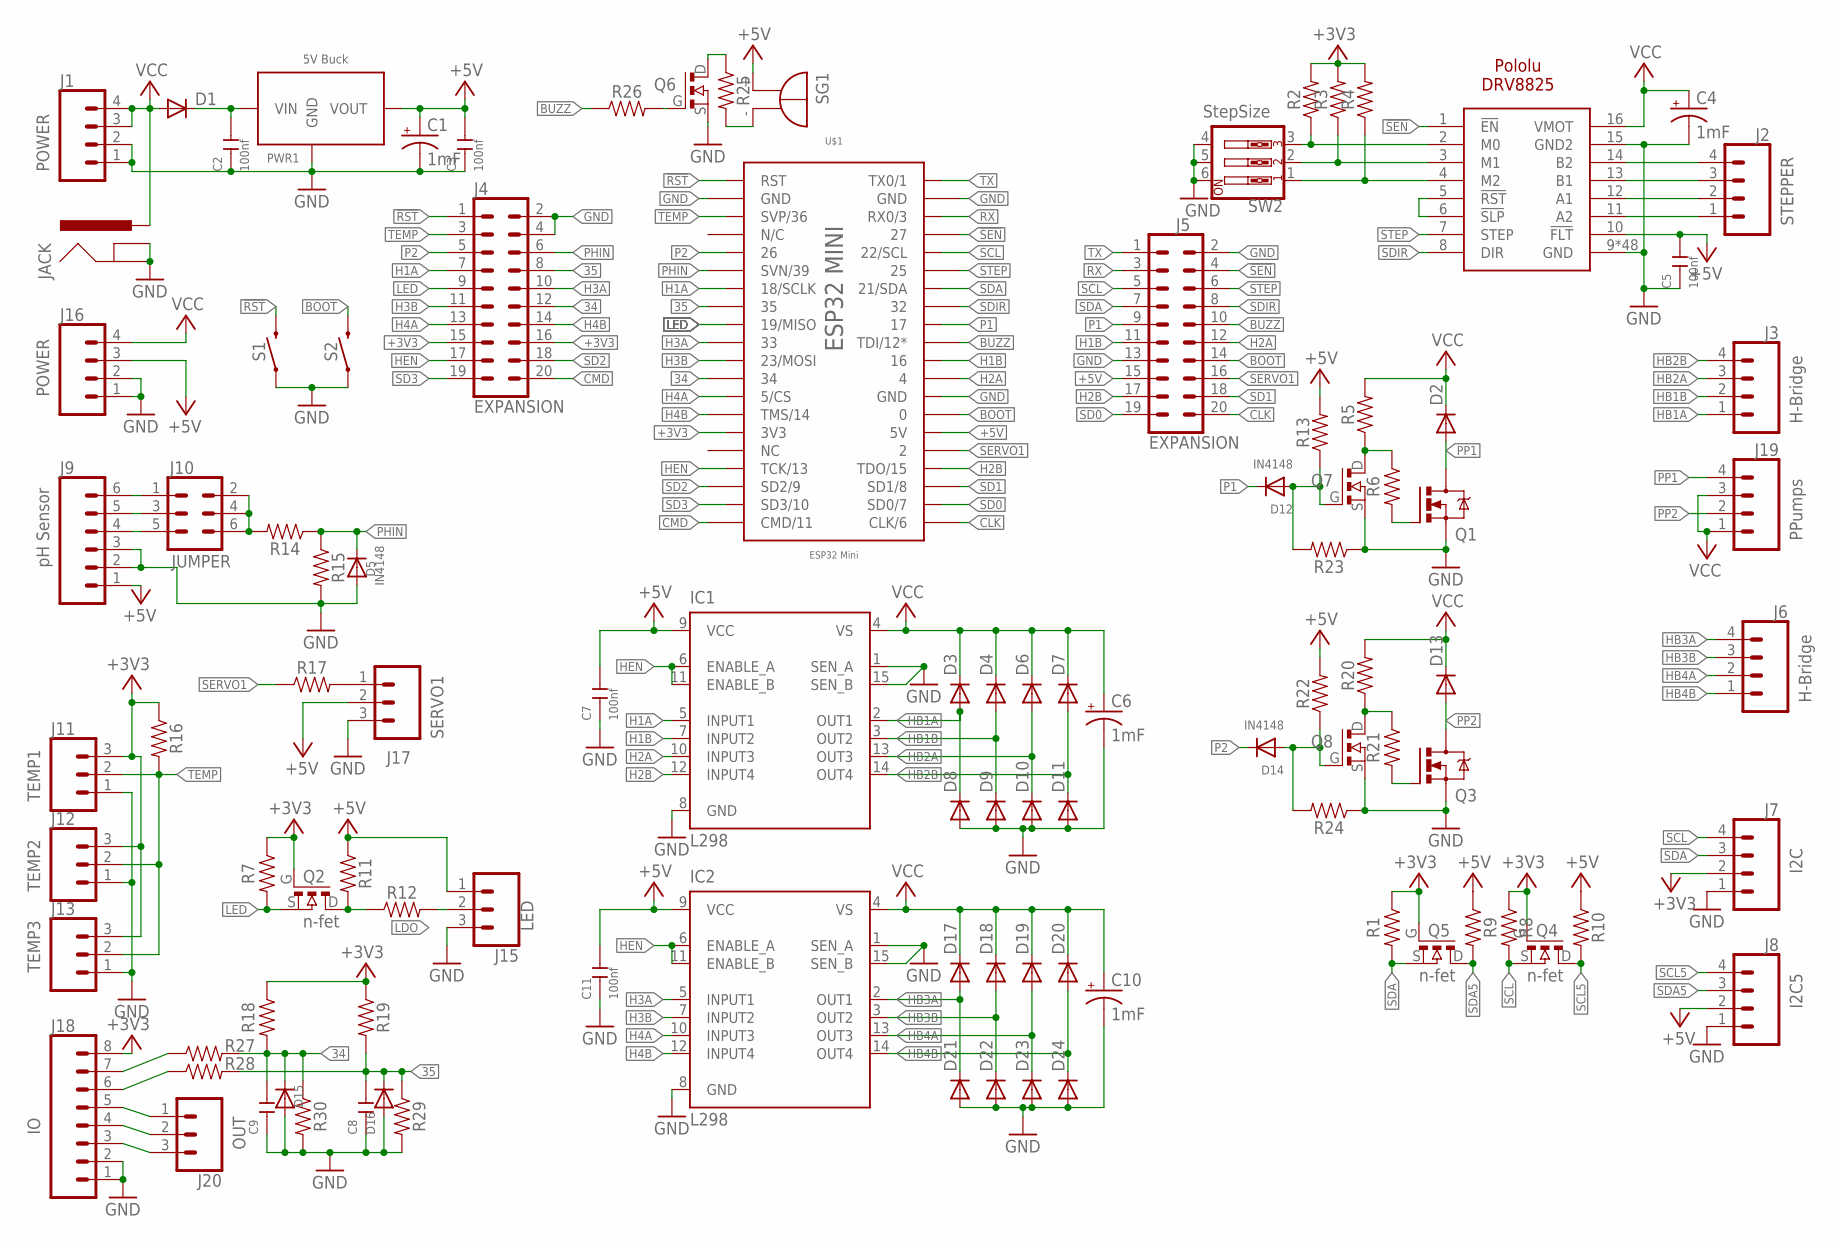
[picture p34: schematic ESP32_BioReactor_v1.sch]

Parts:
C1, C4, C6, C10: 1mF; CPOL-RADIAL-5MM-10MM
C2, C3, C5, C7, C8, C9, C11: 100nf; CERAMIC-2.54
D1, D2, D3, D4, D6, D7, D8, D9, D10, D11, D13, D17, D18, D19, D20, D21, D22, D23, D24: 1N4004; DO41-10
D5, D12, D14, D15, D16: IN4148; DO-1N4148
DR1: DRV8825; POLOLU-DRV8825
IC1, IC2: L298; MULTIWATT-15
J1, J16: POWER; 1X04_LONGPADS
J2: STEPPER; 1X04_LONGPADS
J3, J6: H-Bridge; 1X04_LONGPADS
J4, J5: EXPANSION; 2X10_NOSILK
J7: I2C; 1X04_LONGPADS
J8: I2C5; 1X04_LONGPADS
J9: pH Sensor; 1X06_LONGPADS
J10: JUMPER; 2X3
J11: TEMP1; 1X03_LONGPADS
J12: TEMP2; 1X03_LONGPADS
J13: TEMP3; 1X03_LONGPADS
J15: LED; 1X03_LONGPADS
J17: SERVO1; 1X03_LONGPADS
J18: IO; 1X08_LONGPADS
J19: PPumps; 1X04_LONGPADS
J20: OUT; 1X03
JACK: POWER_JACKPTH_LOCK; POWER_JACK_PTH_LOCK
PWR1: 5V Buck; 5VBUCK
Q1, Q3: IRF740; TO220BV
Q2, Q4, Q5: n-fet; TO92260P520H533-3
Q6, Q7, Q8: 2N7000; TO92260P520H533-3
R1, R2, R3, R4, R5, R6, R7, R8, R9, R10, R11, R12, R13, R14, R15, R16, R17, R18, R19, R20, R21, R22, R23, R24, R25, R26, R27, R28, R29, R30: 10k; AXIAL-0.3
S1, S2: MOMENTARY-SWITCH-SPST-PTH-6.0MM; TACTILE_SWITCH_PTH_6.0MM
SG1: F/HMB
SW2: StepSize; EDG-03
U$1: ESP32 Mini; ESP32MINI

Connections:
34: C9.2, D15.C, J4.12, R18.P$2 (2), R27.P$2 (2), R30.P$1 (1), U$1.34
35: C8.2, D16.C, J4.8, R19.P$2 (2), R28.P$2 (2), R29.P$1 (1), U$1.35
!RST: J4.1, S1.3 (2), U$1.RST
!SEN: DR1.1 (!EN), J5.4, U$1.27
+3V3: J4.15, J4.16, J7.2, J11.3, J12.3, J13.3, J18.8, Q2.G, Q4.G, Q5.G, R1.P$1 (1), R2.P$2 (2), R3.P$2 (2), R4.P$2 (2), R7.P$1 (1), R8.P$1 (1), R16.P$1 (1), R18.P$1 (1), R19.P$1 (1), U$1.3V3
+5V: C1.+, C3.2, C5.2, C7.2, C11.2, DR1.10 (!FLT), IC1.9 (VCC), IC2.9 (VCC), J5.15, J8.2, J9.1, J15.1, J16.3, J17.2, PWR1.VOUT, R9.P$1 (1), R10.P$1 (1), R11.P$1 (1), R13.P$2 (2), R22.P$2 (2), SG1.+, U$1.5V
BOOT: J5.14, S2.3 (2), U$1.0
BUZZ: J5.10, R26.P$1 (1), U$1.TDI (TDI/12*)
CLK: J5.20, U$1.CLK (CLK/6)
CMD: J4.20, U$1.CMD (CMD/11)
GND: C1.-, C2.1, C3.1, C4.-, C5.1, C6.-, C7.1, C8.1, C9.1, C10.-, C11.1, D5.A, D8.A, D9.A, D10.A, D11.A, D15.A, D16.A, D21.A, D22.A, D23.A, D24.A, DR1.9 (GND), DR1.15 (GND2), DR1.GND@1 (GND), DR1.GND@2 (GND), DR1.GND@3 (GND), DR1.GND@4 (GND), DR1.GND@5 (GND), DR1.GND@6 (GND), DR1.GND@7 (GND), DR1.GND@8 (GND), DR1.GND@9 (GND), DR1.GND@10 (GND), DR1.GND@11 (GND), DR1.GND@12 (GND), DR1.GND@13 (GND), DR1.GND@14 (GND), DR1.GND@15 (GND), DR1.GND@16 (GND), DR1.GND@17 (GND), DR1.GND@18 (GND), DR1.GND@19 (GND), DR1.GND@20 (GND), DR1.GND@21 (GND), DR1.GND@22 (GND), DR1.GND@23 (GND), DR1.GND@24 (GND), DR1.GND@25 (GND), DR1.GND@26 (GND), DR1.GND@27 (GND), DR1.GND@28 (GND), DR1.GND@29 (GND), DR1.GND@30 (GND), DR1.GND@31 (GND), DR1.GND@32 (GND), DR1.GND@33 (GND), DR1.GND@34 (GND), DR1.GND@35 (GND), DR1.GND@36 (GND), DR1.GND@37 (GND), DR1.GND@38 (GND), DR1.GND@39 (GND), DR1.GND@40 (GND), DR1.GND@41 (GND), DR1.GND@42 (GND), DR1.GND@43 (GND), DR1.GND@44 (GND), DR1.GND@45 (GND), DR1.GND@50 (GND), DR1.GND@51 (GND), IC1.1 (SEN_A), IC1.8 (GND), IC1.15 (SEN_B), IC2.1 (SEN_A), IC2.8 (GND), IC2.15 (SEN_B), J1.1, J1.2, J4.2, J4.4, J5.2, J5.13, J7.1, J8.1, J9.2, J9.3, J11.1, J12.1, J13.1, J15.3, J16.1, J16.2, J17.3, J18.1, J18.2, JACK.GND, JACK.GNDBREAK, PWR1.GND, Q1.S, Q3.S, Q6.S, Q7.S, Q8.S, R15.P$2 (2), R23.P$1 (1), R24.P$1 (1), R29.P$2 (2), R30.P$2 (2), S1.1, S2.1, SW2.4, SW2.5, SW2.6, U$1.GND@1 (GND), U$1.GND@2 (GND), U$1.GND@3 (GND)
H1A: IC1.5 (INPUT1), J4.7, U$1.18 (18/SCLK)
H1B: IC1.7 (INPUT2), J5.11, U$1.16
H2A: IC1.10 (INPUT3), J5.12, U$1.4
H2B: IC1.12 (INPUT4), J5.17, U$1.TDO (TDO/15)
H3A: IC2.5 (INPUT1), J4.10, U$1.33
H3B: IC2.7 (INPUT2), J4.11, U$1.23 (23/MOSI)
H4A: IC2.10 (INPUT3), J4.13, U$1.5 (5/CS)
H4B: IC2.12 (INPUT4), J4.14, U$1.TMS (TMS/14)
HB1A: D3.A, D8.C, IC1.2 (OUT1), J3.1
HB1B: D4.A, D9.C, IC1.3 (OUT2), J3.2
HB2A: D6.A, D10.C, IC1.13 (OUT3), J3.3
HB2B: D7.A, D11.C, IC1.14 (OUT4), J3.4
HB3A: D17.A, D21.C, IC2.2 (OUT1), J6.4
HB3B: D18.A, D22.C, IC2.3 (OUT2), J6.3
HB4A: D19.A, D23.C, IC2.13 (OUT3), J6.2
HB4B: D20.A, D24.C, IC2.14 (OUT4), J6.1
HEN: IC1.6 (ENABLE_A), IC1.11 (ENABLE_B), IC2.6 (ENABLE_A), IC2.11 (ENABLE_B), J4.17, U$1.TCK (TCK/13)
LDO: J15.2, R12.P$2 (2)
LED: J4.9, Q2.S, R7.P$2 (2), U$1.19 (19/MISO)
unnamed: DR1.3 (M1), R3.P$1 (1), SW2.2
unnamed: C2.2, D1.C, PWR1.VIN
unnamed: DR1.4 (M2), R4.P$1 (1), SW2.1
unnamed: Q7.D, R5.P$1 (1), R6.P$1 (1)
unnamed: DR1.5 (!RST), DR1.6 (!SLP)
unnamed: J10.2, J10.4, J10.6, R14.P$2 (2)
unnamed: Q1.G, R6.P$2 (2)
unnamed: DR1.2 (M0), R2.P$1 (1), SW2.3
unnamed: Q8.D, R20.P$1 (1), R21.P$1 (1)
unnamed: R25.P$2 (2), SG1.-
unnamed: Q3.G, R21.P$2 (2)
unnamed: DR1.11 (A2), J2.1
unnamed: DR1.12 (A1), J2.2
unnamed: DR1.13 (B1), J2.3
unnamed: DR1.14 (B2), J2.4
unnamed: D14.A, Q8.G, R22.P$1 (1), R24.P$2 (2)
unnamed: J9.4, J10.5
unnamed: Q6.D, R25.P$1 (1)
unnamed: Q6.G, R26.P$2 (2)
unnamed: J9.5, J10.3
unnamed: J9.6, J10.1
unnamed: D12.A, Q7.G, R13.P$1 (1), R23.P$2 (2)
unnamed: Q2.D, R11.P$2 (2), R12.P$1 (1)
unnamed: J17.1, R17.P$2 (2)
unnamed: J18.5, J20.1
unnamed: J18.4, J20.2
unnamed: J18.3, J20.3
unnamed: J18.6, R28.P$1 (1)
unnamed: J18.7, R27.P$1 (1)
P1: D12.C, J5.9, U$1.17
P2: D14.C, J4.5, U$1.26
PHIN: D5.C, J4.6, R14.P$1 (1), R15.P$1 (1), U$1.SVN (SVN/39)
PP1: D2.A, J19.4, Q1.D
PP2: D13.A, J19.2, Q3.D
RX: J5.3, U$1.RX0 (RX0/3)
SCL: J5.5, J7.4, Q4.S, R8.P$2 (2), U$1.22 (22/SCL)
SCL5: J8.4, Q4.D, R10.P$2 (2)
SD0: J5.19, U$1.SD0 (SD0/7)
SD1: J5.18, U$1.SD1 (SD1/8)
SD2: J4.18, U$1.SD2 (SD2/9)
SD3: J4.19, U$1.SD3 (SD3/10)
SDA: J5.7, J7.3, Q5.S, R1.P$2 (2), U$1.21 (21/SDA)
SDA5: J8.3, Q5.D, R9.P$2 (2)
SDIR: DR1.8 (DIR), J5.8, U$1.32
SERVO1: J5.16, R17.P$1 (1), U$1.2
STEP: DR1.7 (STEP), J5.6, U$1.25
TEMP: J4.3, J11.2, J12.2, J13.2, R16.P$2 (2), U$1.SVP (SVP/36)
TX: J5.1, U$1.TX0 (TX0/1)
VCC: C4.+, C6.+, C10.+, D1.A, D2.C, D3.C, D4.C, D6.C, D7.C, D13.C, D17.C, D18.C, D19.C, D20.C, DR1.16 (VMOT), IC1.4 (VS), IC2.4 (VS), J1.3, J1.4, J16.4, J19.1, J19.3, JACK.PWR, R5.P$2 (2), R20.P$2 (2)

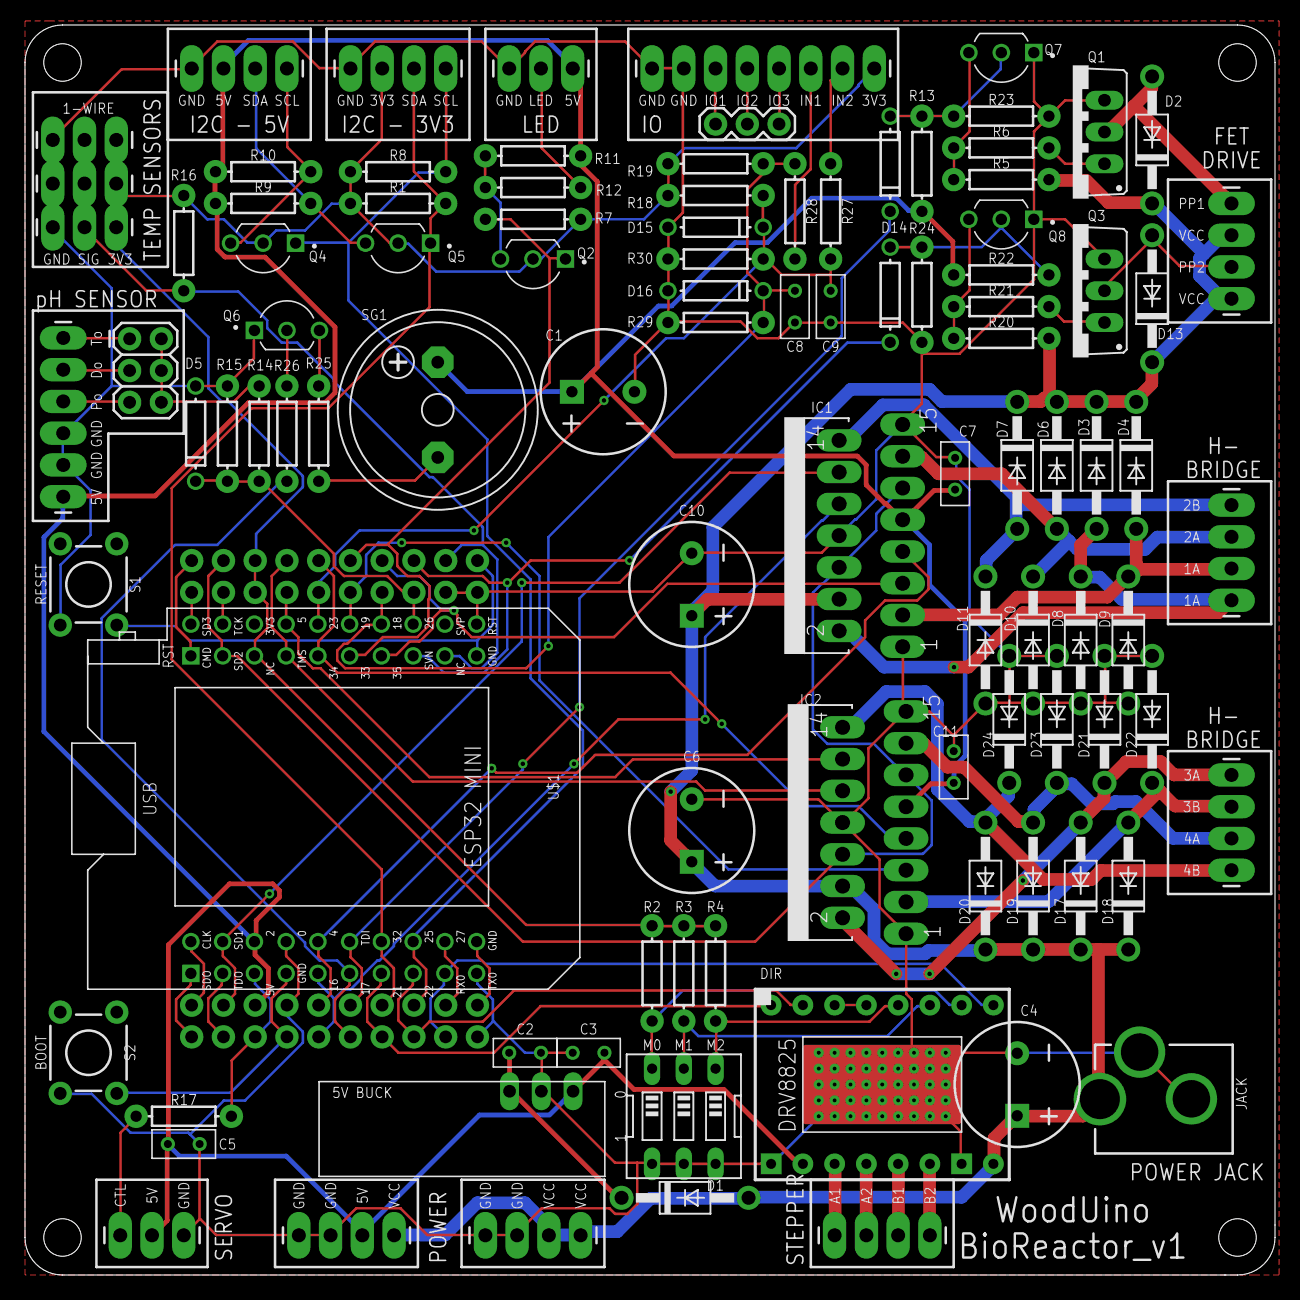
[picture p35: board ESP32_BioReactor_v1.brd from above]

Board: 2 copper layers, 100.0 x 100.0 mm, 102 parts (0 on the bottom side), 79 nets.

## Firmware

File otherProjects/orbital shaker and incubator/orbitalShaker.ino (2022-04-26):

//copyright 2021 Adrian F
//will OpenSource once stabile and published
//FOR MAKERBASE BOARD :           C:\a\diy\eagle\makerBaseDlc32v2.1.002/MKS_DLC32 _V2.1_002_SCH.pdf
//int pins[] = { 2, 5,23, 25, 26, 27, /*32 is the spindle heater*/ 33 };// LED, 5=EXT1-3, 23=EXT2-6, 25=EXT1-7, 26=EXT1-5, 27=EXT1-4 or 8
#include "Arduino.h"
#include <Melody.h>
#include <DHTesp.h> //for DHT temp sensor
//memory card https://www.mischianti.org/2021/03/28/how-to-use-sd-card-with-esp32-2/
// include the SD library:
#include <SPI.h>
#include <SD.h>
#include <FS.h>
//Suggest SD card: Class4 or Class10; 4~16G memory; Fat32 format. File format support: .NC; .GC; .GCODE
//SD memory card D0=IO2,DI=IO13,CK=IO14,CS=IO15,DET=IO39  file:///C:/a/diy/eagle/makerBaseDlc32v2.1.002/MKS-DLC32-main/hardware/MKS%20DLC32%20V2.1_002/MKS%20DLC32%20V2.1_002%20PIN.pdf
/* Pins_Arduino_h */
//music
#define SERIAL_BAUDRATE 115200
//we use PROBE_PIN=22 for stepper because we want to use so connect PROBE S to DR8825
//for temperature sensor use GND and 5 Volt from Probe connector and DAT to DHT_PIN=19 which is on extension LCD_MISO
//for speaker we use GND and on + in series with 100  OHM we use GPIO23 which is LCD_MOSI
//
// for motor current // Vref = Imax /2
//for m17hs16-2004s1 https://www.omc-stepperonline.com/nema-17-bipolar-45ncm-64oz-in-2a-42x42x40mm-4-wires-w-1m-cable-connector-17hs16-2004s1 and Imax=2 AMp hold torque=Holding Torque: 45Ncm(64oz.in)
//and https://www.youtube.com/watch?v=BV-ouxhZamI
//  to measure on screw-driver=2*8*.068 about 1 volt but I'll go less maybe .9 volts
enum {
	HEATER_PIN = 32, HEATER_PWM_CHANNEL = 0, STEPPER_PWM_STEP_PIN = 22/*probe pin*/, STEPPER_PWM_CHANNEL = 2,/*NOT USED I2SO_BUZZ_PIN = 0000???,*/
	I2SO_DATA_PIN = 21, I2SO_CLOCK_PIN = 16, I2SO_LATCH_PIN = 17, LED_PIN = 2, POTENTIOMETER_PIN = 777777, DHT_PIN = 19/* LCD_MISO*/, TURN_ON_STEPPER_PIN = 36/*Sensor_VP SVP -*/, SPEAKER = 23, /*LCD_MOSI*/SPEAKER_CHANNEL = 4, FAN_PIN = 33/*LCD_RS*/, FAN_PWM_CHANNEL = 6, MEMORY_CS_PIN = 15
};
//
enum {
	TIMESTAMP = true, TEMP_DISPLAY = true,
};
//
enum {
	DEBUG_HEATER = true, DEBUG_SWITCH = true, DEBUG_LOW_HUMIDITY = true
};
//FAN https://fdossena.com/?p=ArduinoFanControl/i.md
//timer
//temperature sensor stuff
const float MODERATED_HEAT_POWER = 0.8;
DHTesp dht;
int lastTempHumidityReadTime = 0; //never
int lastAlertTime = 0; //never
float desiredTemperature = 37.0; //seed it
float oldTemperature = 0.;
float minHumidity = 60.;
boolean heaterWasOn = false;
boolean firstTimeTurnOnHeater = true;
boolean firstTimeReachDesiredTemperature = true;
int maxTemperature = 0;
//motor
// what we want for OS motor
//https://github.com/nenovmy/arduino/blob/master/leds_disco/leds_disco.ino
double desiredRPM = 300;
int freq = (int) desiredRPM / 60 * 200;
/* Setting motor PWM Properties */
const int PWMResolution = 10;
const int MAX_DUTY_CYCLE = (int) (pow(2, PWMResolution) - 1);
//fan
const int halfDutyCycle = MAX_DUTY_CYCLE / 2;
const float fanDutyCyclePercentage = 1;
const int FAN_FREQUENCY = 40000;
int maxHeaterDutyCycle = MAX_DUTY_CYCLE * .75; // 80x100mm 12V DC 20W Silicone Heated Bed Heating Pad
//de-bounce variables
const int DEBOUNCE_TIME = 200;
unsigned long lastDebounceTime = 0;
int lastSteadyState = LOW; // the previous steady state from the input pin
int lastFlickerableState = -100; // the previous flicker-able state from the input pin
int lastButtonState; // the current reading from the input pin which could be unreliable due to vibration
//music
Melody scaleLouder("c>>> d>> e>f g< a<< b<<< c*<<<<", 480);
Melody invalidChoice(" (cg_)__");
Melody validChoice(" (cgc*)**---");
Melody frereJacques("(cdec)x2   (efgr)x2;//   ((gagf)-ec)x2     (c g_ c+)x2");
Melody frereJacquesFull("(cdec)x2   (efgr)x2  ((gagf)-ec)x2     (c g_ c+)x2");
Melody auClairDeLaLune("cccde+dr  ceddc+.r");
Melody darthVader(
		" (ggg e,-. b,-- | g e,-. b,-- g+ (ddde,-.)* b,--  | g, e,-. b,-- g+ | g* g-.g--  (g g,-. f-- (ed#)-- e-)* r- g#- c#* b#-.b-- |  (b,a)-- b,- r- e,- g, e,-. g,-- | b, g-. b,-- d*+  | g* g-.g--  (g g,-. f-- (ed#)-- e-)* r- g#- c#* b#-.b-- |  (b,a)-- b,- r- e,- g, e,-. b,-- | g e,-. b,-- g+ |)<<_ ");
//time
unsigned long startTime = millis(); //in ms
//SD memory card
const int32_t SPIfreq = 40000;
//
void setup() {
	Serial.begin(115200);
	Serial.println("=================================setup starting now=============================");
	// Declare pins as output:
	pinMode(LED_PIN, OUTPUT);
	pinMode(STEPPER_PWM_STEP_PIN, OUTPUT);
	pinMode(I2SO_LATCH_PIN, OUTPUT);
	pinMode(I2SO_CLOCK_PIN, OUTPUT);
	pinMode(I2SO_DATA_PIN, OUTPUT);
	//pinMode(FAN_PIN, OUTPUT);
	pinMode(TURN_ON_STEPPER_PIN, INPUT);
	pinMode(SPEAKER, OUTPUT);
	alternate(LED_PIN, 50, 5);
	// speaker
	ledcSetup(SPEAKER_CHANNEL, 5000, 8);
	ledcAttachPin(SPEAKER, SPEAKER_CHANNEL);
	ledcWrite(SPEAKER_CHANNEL, 0); //duty Cycle = 0
	play(validChoice);
	// temperature sensor
	dht.setup(DHT_PIN, DHTesp::DHT22);
	Serial.println("DHT initiated");
	//heater
	pinMode(HEATER_PIN, OUTPUT);
	//setup the heater
	ledcSetup(HEATER_PWM_CHANNEL, 40000, PWMResolution);
	delay(20);
	ledcAttachPin(HEATER_PIN, HEATER_PWM_CHANNEL);/* Attach the STEP_PIN PWM Channel to the GPIO Pin */
	delay(20);
	Serial.println("stepper target speed at RPM :");
	Serial.println(desiredRPM);
	//motor
	Serial.println("Initial disabling of the stepper in setup");
	stopStepper();
	play(scaleLouder);
	fanSetup();
	//setupSDCard();
	Serial.println("=================================END Setup==================================");
}
//
void loop() {
	int stepperButtonPosition = readTurnOnStepper();
	if (stepperButtonPosition == 1) {
		startStepper();
		fanOff(true);
	} else {
		if (stepperButtonPosition == 0) {
			stopStepper();
			fanOn(true);
		}
	}
	// Get temperature
	int temperature;
	int humidity;
	if (((millis() - lastTempHumidityReadTime) / 1000) > 2) { // every 2 seconds
		getTemperature(temperature, humidity);
		lastTempHumidityReadTime = millis();
		if (temperature > maxTemperature) {
			maxTemperature = temperature;
		}
		if (TEMP_DISPLAY) {
			Serial.print("Temp: " + String(temperature) + " Celsius,  Humidity: " + String(humidity) + "% maximum temperature: " + String(maxTemperature));
			if (TIMESTAMP) {
				Serial.println(" after: " + getFormatedTimeSinceStart());
			} else {
				Serial.println("");
			}
		}
		if (temperature < desiredTemperature) {
			if (firstTimeTurnOnHeater) {
				play(auClairDeLaLune);
				firstTimeTurnOnHeater = false;
			}
			digitalWrite(LED_PIN, HIGH);
			if (desiredTemperature - temperature >= 2) {
				if (TEMP_DISPLAY) {
					Serial.println("Heat on at full power");
				}
				ledcWrite(HEATER_PWM_CHANNEL, maxHeaterDutyCycle);
			} else {
				if (TEMP_DISPLAY) {
					Serial.print("Heat on at ");
					Serial.print(MODERATED_HEAT_POWER * 100);
					Serial.println("% power");
				}
				ledcWrite(HEATER_PWM_CHANNEL, maxHeaterDutyCycle * MODERATED_HEAT_POWER);
			}
			heaterWasOn = true;
		} else { // no need to heat
			if (heaterWasOn) { // was on before this, used to stop printing too many times
				Serial.println("Heater OFF");
				heaterWasOn = false;
				if (firstTimeReachDesiredTemperature) {
					play(frereJacquesFull);
					firstTimeReachDesiredTemperature = false;
				} else
					play(frereJacques);
			}
			digitalWrite(LED_PIN, LOW);
			ledcWrite(HEATER_PWM_CHANNEL, 0); // turn heater off
			if (humidity < minHumidity && ((millis() - lastAlertTime) / 1000) > 200/* about 3 minutes*/) {
				Serial.println("WARNING !!! humidity dropped less then minimal humidity");
				lastAlertTime = millis();
				if (DEBUG_LOW_HUMIDITY) {
					play(invalidChoice);
				}
			}
		}
	}
}
//
void startStepper() {
	Serial.println("START STEPPER");
	setupI2SOShiftEnableMotor();
	for (int f = freq * .6; f < freq * .7; f += 5) {
		ledcSetup(STEPPER_PWM_CHANNEL, f, PWMResolution);
		//delay(5);
		ledcAttachPin(STEPPER_PWM_STEP_PIN, STEPPER_PWM_CHANNEL);/* Attach the STEP_PIN PWM Channel to the GPIO Pin */
		//delay(5);
		ledcWrite(STEPPER_PWM_CHANNEL, halfDutyCycle);
		delay(200);
	}
	for (int f = freq * .7; f <= freq; f += 100) {
		ledcSetup(STEPPER_PWM_CHANNEL, f, PWMResolution);
		//delay(5);
		ledcAttachPin(STEPPER_PWM_STEP_PIN, STEPPER_PWM_CHANNEL);/* Attach the STEP_PIN PWM Channel to the GPIO Pin */
		//delay(5);
		ledcWrite(STEPPER_PWM_CHANNEL, halfDutyCycle);
		delay(100);
	}
//play(auClairDeLaLune);
}
//
void stopStepper() {
	Serial.println("STOP STEPPER");
	setupI2SOShiftDisableMotor();
	ledcDetachPin(STEPPER_PWM_STEP_PIN);/* Detach the STEP_PIN PWM Channel to the GPIO Pin */
	delay(200);
}

int getTemperature(int &temp, int &humid) {
// Reading temperature for humidity takes about 250 milliseconds!
// Sensor readings may also be up to 2 seconds 'old' (it's a very slow sensor)
	TempAndHumidity newValues = dht.getTempAndHumidity();
// Check if any reads failed and exit early (to try again).
	if (dht.getStatus() != 0) {
		Serial.println("DHT12 error status: " + String(dht.getStatusString()));
		play(auClairDeLaLune);
		return false;
	}
	temp = newValues.temperature;
	if (temp < 0 || temp > 70) {
		for (int i = 0; i < 10; i++) {
			play(darthVader);
		}
	}
	humid = newValues.humidity;
	return true;
}

// current https://reprap.org/wiki/NEMA_17_Stepper_motor 17hs16 20044s1(black ones) rated for 2 A
// adjustment guide https://lastminuteengineers.com/drv8825-stepper-motor-driver-arduino-tutorial/ Vref on Pot = max current /2 =1V
// xDir is 2 xStep is 1 and beeper is 7
void setupI2SOShiftEnableMotor() {
	//Serial.println("#################### setupI2SOShift   EnableMotor #####################################");
	byte bits[16] = { 0, 1, 1, 1, 1, 1, 1, 1, 1, 1, 1, 1, 1, 1, 1, 0 }; //enable is pin 0 and should be low to start stepper, last one is the beeper
	writeData(bits);
	delay(100);
}
//
void setupI2SOShiftDisableMotor() {
	//Serial.println("#################### setupI2SOShift    DisableMotor #####################################");
	byte bits[16] = { 1, 1, 1, 1, 1, 1, 1, 1, 1, 1, 1, 1, 1, 1, 1, 0 }; //enable is pin 0 and should be high to stop stepper, last one is the beeper
	writeData(bits);
	delay(10);

}
//
void writeData(byte *bits) {
//alternate data we can just capture the 2 data values like 2254, 2124
	int data1 = 0;
	for (int i = 0; i < 8; i++) {
		data1 |= bits[i + 8] << i;
	}
	int data2 = 0;
	for (int i = 0; i < 8; i++) {
		data2 |= bits[i] << i;
	}
// disable update
	digitalWrite(I2SO_LATCH_PIN, LOW);
// shift out the data (second shift register must be send first)
	shiftOut(I2SO_DATA_PIN, I2SO_CLOCK_PIN, MSBFIRST, data1); // NOT NEEDED FOR X axes
//Serial.print("data2");Serial.println(data2);
	shiftOut(I2SO_DATA_PIN, I2SO_CLOCK_PIN, MSBFIRST, data2); //*
// update the shift register output pins
	digitalWrite(I2SO_LATCH_PIN, HIGH);
}

//
void alternate(int pin, int de, int times) {
//	Serial.println("alternate on pin:");
//	Serial.println(pin);
	for (int var = 0; var < times; ++var) {
		digitalWrite(pin, HIGH);
		delay(de);
		digitalWrite(pin, LOW);
		delay(de);
	}
}

// Function for reading the Potentiometer
int readPotentiometer() {
	int customDelay = analogRead(POTENTIOMETER_PIN); // Reads the potentiometer
	int newRPM = map(customDelay, 0, 1023, 0, 300); //read values of the potentiometer from 0 to 1023 into  d0->300
	return 300;
}

// WeMos D1 esp8266: D8 as standard
const int chipSelect = SS;

void printDirectory(File dir, int numTabs);

void setupSDCard() {
	Serial.print("\nInitializing SD card...");
	SPIClass hspi = SPIClass(HSPI); //HSPI has the 12-15 pins already configured // actually a reference
	if (!SD.begin(MEMORY_CS_PIN, hspi, SPIfreq, "/sd", 2)) { //copied from Fluid SDCard.cpp //if (SD.begin(csPin, SPI, SPIfreq, "/sd", 2)) {
		Serial.println("initialization failed. Things to check:");
		Serial.println("* is a card inserted?");
		while (1)
			;
	} else {
		Serial.println("A card is present.");
	}
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

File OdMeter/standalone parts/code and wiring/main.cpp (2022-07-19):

// Reference implementation for Optical Density Meter using an Arduino nano
//Wiring info at the end of this file
// works for arduino nano
// work-dir index head
// main code for the Optical density meter
// current project hosted in Visual Source Code
#include <Arduino.h>
#include <EEPROM.h>
#include <SPI.h>
#include <Wire.h>
#include <BH1750.h>  //NEEDS TO BE AFTER WIRE
#include <main.h>  

int BH17_add = 0x23;  // I2C address of BH1750 https://www.mouser.com/datasheet/2/348/bh1750fvi-e-186247.pdf  Small measurement variation (+/- 20%)
uint32_t buffer = 0;
boolean oldCalibration = true;
const uint32_t lowLightTreshold = 20;
unsigned long warmupTime = 15 * 60000;  // in milliseconds for some reasons it does not like 15*60*1000
// commands
int arg = 0;

const boolean DEBUG_MODE=true;
const int BUFER_WRITING_EEPROM_ADDRESS = 0;
// see electronics at the end
/* Usage Instructions
 cover the instrument to measure less than 20 lux does a reset
 wait from prompt
 insert cuvette with buffer to read blank value and wait for next prompt
 insert sample.
 You can run it without a display using a serial cable and a terminal program like coolTerm.
 You can even type commands terminated by new line like b and a new value for the buffer value.
 */

BH1750 lightSensor(0x23);

void setup() {
    Serial.begin(115200);
    Serial.print("In setup ");
    Wire.begin();
    if (lightSensor.begin(BH1750::CONTINUOUS_LOW_RES_MODE)) {
        Serial.println(F("BH1750 Advanced begin"));
    } else {
        Serial.println(F("Error initialising BH1750"));
    }
    Serial.println("Finished waking up");
    EEPROM.get(BUFER_WRITING_EEPROM_ADDRESS, buffer);
    delay(500);
    Serial.println("Finished setup");
}
//
void loop() {
    uint32_t sampleLux = readLight(100);
    if(DEBUG_MODE) {
      Serial.print("lux:");
      Serial.println(sampleLux);
      return;
    }
    if (sampleLux < lowLightTreshold) {
        buffer = 0;
        calibrate(sampleLux);
    }
    Serial.print("OD:");
    Serial.print(-log10((double)sampleLux / buffer));
    Serial.print("   Sampl:");
    Serial.print(sampleLux);
    if (oldCalibration) {
        Serial.print("  Buffer (old):");
    } else {
        Serial.print("  Buffer:");
    }
    Serial.print(buffer);
    Serial.print("  sample/buffer:");
    Serial.print((double)sampleLux / buffer);
    if (warmupTime > millis()) {
        unsigned long timeLeft = warmupTime - millis();
        Serial.print(" WARMING UP for another:");
        // Serial.print((int) (((double) timeLeft) / 60000.));
        Serial.print((int)(timeLeft / 60000.));
        Serial.print(" minutes, ");
        Serial.print((int)(((timeLeft) % 60000) / 1000));
        Serial.println(" seconds");
    }
    Serial.println(" after:" + getFormatedTimeSinceStart());
    checkForCommand();
    delay(250);
}
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

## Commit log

2020-04-10 Rename ESP_with_eclipse.md to Configuring Eclipse to run ESP32.md
2020-04-22 temperature reading & websockets
2020-05-07 ph sensor
2020-05-27 join sensor code
2020-06-04 Update Configuring Eclipse to run ESP32.md
2020-06-14 fixed temp sensor
2020-12-14 move motor code to actuators
2021-01-08 read only one temp sensor
2021-01-30 calibrating ph
2021-02-25 running stepper in separate thread
2021-02-25 run motor without running the program
2021-03-13 sensor update rate and readings collectioin
2021-11-08 store sensor readings
2021-12-18 fix bug with enabling motor
2022-02-11 changed sensor reading cache
2022-03-16 Main bioreactor board version 1.1 and potentistat board 1.0
    The main board in Eagle format including documentation pdfs
    also the full breakout board for reading the dissolved Oxigen via a potentiostat device
    [ESP32_BioReactor_v1.brd, ESP32_BioReactor_v1.sch]
2022-03-16 moved external documentation in GitHub
    moved external documentation in GitHub
    [OD reader 16 (13).stl, rocker parts 19 (4).stl]
2022-03-16 moved documents from other storage
    [peristaltic.scad]
2022-03-16 moved documents from Google Drive and other sources
    [BOM Wave Bioreactor V2.ods]
2022-03-16 moved to gitHub
    [b55 YET another copy v2.f3d]
2022-03-16 Orbital shaker box and box generator script
    [script OS 23 v1.f3d]
2022-03-17 support motor rpm
2022-03-22 added BOM
    [script OS 23 v1.f3d]
2022-03-22 added some screenshots
    added some screenshots
    [Links big screw 10 v8.f3d]
2022-03-23 separated wet components
    separated wet components
    [BOM Wave Bioreactor V2.ods, BOM Wave Bioreactor for Danny Chan.ods]
2022-03-23 wet parts changes
    wet parts changes
    [BOM Wave Bioreactor V2.ods, BOM Wave Bioreactor for Danny Chan.xlsx]
2022-03-23 Create enz one two parts 2 v3.f3d
    holder + tube +mold for washer
    [enz one two parts 2 v3.f3d]
2022-03-25 updates
    updates
    [enz one part 0 v1.f3d, enz one two parts 4 v4.f3d]
2022-04-02 update
    update
    [enz one part 0 v8.f3d]
2022-04-14 results in running the OS for > 8 hours at 300 RPM with 50ml LB media in 100ml flask
    results in running the OS for > 8 hours at 300 RPM with 50ml LB media in 100ml flask
2022-04-19 some fuGFP and OpticalDensity data
    [Links big screw 10 v8.f3d, chart of variations in OD fuGFP at 37 for 24 hours.ods, script OS 23 v1.f3d]
2022-04-21 more stuff for the OS
    [OS backing board brackets v16.f3d, flaskholder100ml v4.f3d, script OS 25 v8.f3d]
2022-04-22 winged nuts
    [OS backing board brackets v22.f3d, WingedNutThroughScrew v3.f3d]
2022-06-09 Backup of FUsion360 on June 8th
    Backup of FUsion360 on June 8th
    [1 OINT 4 test fit WITH 2 MM TOOLDIAM PARAM_v4.f3d, 1 element test fit 1 4_v11.f3d, 12 bioreactor 6 mm finger almost manufacture_v8.f3d, 15 bioreactor 10 mm_v7.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]
2022-06-16 new box and smaller axis and big case for standalone Optical density meter
    [b61 2mm CUT successfuly v1.f3d, optical density standalone 4 v4.f3d, optical density standalone 4 v8.f3d, pillows small ballbearing close screws 1 v7.f3d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]
2022-06-22 mostly documentation
    mostly documentation
    [1 OINT 4 test fit WITH 2 MM TOOLDIAM PARAM_v4.f3d, 1 element test fit 1 4_v11.f3d, 12 bioreactor 6 mm finger almost manufacture_v8.f3d, 15 bioreactor 10 mm_v7.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]
2022-07-12 more images
    [Links big screw 10 v8.f3d, OD case jenny.stl, OD interior Jenny.stl, OD lid jenny.stl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]

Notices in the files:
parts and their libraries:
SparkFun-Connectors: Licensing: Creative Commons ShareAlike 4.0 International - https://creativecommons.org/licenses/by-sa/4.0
